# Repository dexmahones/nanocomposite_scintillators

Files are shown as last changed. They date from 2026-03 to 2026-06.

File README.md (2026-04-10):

# Scintillators for Low-Cost Pet
Documentation for a project to develop low-cost nanocomposite scintillator pixels for a PET scanner prototype. The purpose for these notes is primarily as a means of collating findings, data and progress into one piece of IP to facilitate continuity between different stages of the project. This repository consists of the following categories.
## Context
Details on the relevant theory, methodology and progress are stored in the root directory. Key notes are listed below, with links to relevant subsidiary notes embedded in them.  
- [Introduction](Introduction.md)
- [Positron Emission Tomography](PositronEmissionTomography.md)
- [Scintillator Landscape](Scintillator%20Landscape.md)
- [Scintillator Design Considerations](Scintillator%20Design%20Considerations)
- [Characterization Methods](Characterization)
## References
A growing list of [References](References.md) to useful resources is included as a kind of database of the literature consulted during the course of the project.
## Logbook
A list of the pixel fabrication techniques and trials that have already been attempted can be found in the [Fabrication Log](Logbook.md), which should be updated with any new developments.
## Manuals
A folder containing documentation and manuals (listed in [Manuals](Manuals)) for essentially any externally procured products. This includes any measurement instruments, industry standard scintillator pixels, chemical safety datasheets, quotes etc. 
## Figures
A folder to store any generated figures, both for ease of access and for embedding in these notes. 
## Data
A folder for all data taken during characterization and experimentation. 
## Code
The codebase used for this project, including data analysis, instrument control and figure generation. [Documentation](Documentation) for the code is currently in progress.
## Progress Reports
Biannual reports detailing the last six months of progress. Typically to be submitted to funders.

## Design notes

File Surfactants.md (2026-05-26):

*a.k.a ligands, capping agents*
Molecules that encapsulate nanoparticles and prevent them from aggregating. As an example, consider the CdS and CdSe nanoparticles that have been synthesized. As I understand it, two capping agents have been used, namely [oleylamine](#Oleylamine) and [oleic acid](#oleic%20acid). They are typically used to suspend the nanoparticles in [octadecene](#octadecene) and/or [toluene](#toluene) solvents. 
## Oleylamine
#ligand
- Exhibits affinity to metals through NH2 functional groups. 
- Acts as strong reducing agent as well as a stabilizer in the synthesis of nanoparticle.
![[oleylamine_structure.png]]
## Oleic Acid
#ligand
- Widely used as a surfactant for the stabilization of magnetic nanoparticles.
- Carboxyl group binds to metallic NPs in one of a number of different configurations.
![[oleic_acid_structure.png]]
## BMEP
#ligand 
- Hydrophilic monomer 
- Two polymerizable methacrylate groups 
- Centrally placed phosphate group that binds to NPs.
- It is widely used as a precursor in the synthesis of poly (BMEP), dental resins, hydrogels, and fire-retardant polymer composites.
![[bmep_structure.avif]]
Following a paper by [[References#jin2016partial|Jin et al.]] in 2016. 
- Partially exchanged OA capping YbF3 NPs with BMEP for copolymerization with PVT
![[bmep_oa_partial_exchange.png]]
### Chemicals 
- Oleic acid (OA, 90%)
- 1-octadecene (ODE, 90%), 
- ytterbium oxide (99.9%), 
- `bis[2-(methacryloyloxy)ethyl] phosphate (BMEP)`,
- vinyl toluene (VT, 99%,), 
- divinylbenzene (DVB, 80%), 
- 2-(4-tertbutylphenyl)-5-(4-biphenylyl)-1,3,4-oxadiazole (b-PBD, 99%) 
- 1,4-bis(5-phenyloxazol-2-yl) benzene (POPOP) 
- trifluoroacetic acid (TFA)
- 1,1-bis(tertbutylperoxy)-3,3,5-trimethylcyclohexane (DTTMC, 75% in aromatic free mineral spirit)
- EJ-212
### Precursor Yb(CF3COO)3 synthesis 
- Yb2O3 (10 g) powder, trifluoroacetic acid (23 ml) and DI water (23 ml) added to 250 ml flask. 
- Heated to 65°C stirred for 10 h.
- Excess trifluoroacetic acid removed by rotation evaporation to get white powder.
- Powder then dried by purging with dried argon under heating for 2 h.  
### YbF3 NP synthesis  
- Oleic acid (33.9 g) and 1-octadecene (30.3 g) added to 250 ml three-neck flask
- Degassed under vacuum for several minutes with periodic argon purging. 
- Yb(CF3COO)3 (3 g) added into the mixture under argon. 
- Solution heated to 100°C in 30 min under argon
- Vacuum pumping applied for several minutes to remove residual water and oxygen. 
- Solution was rapidly heated to 304°C and maintained at this temperature for 45 min. 
- Mixture was cooled to room temperature
- ==NPs were precipitated by the addition of acetone/hexane (4 : 1 v/v) and isolated via centrifugation at a speed of 7000 rpm for 5 min.== 
- Resulting white powder washed with ethanol three times and dried under vacuum. 
- Resulting NPs could dissolve in a low-polarity solvent well.  
### Ligand exchange of oleic acid-stabilized YbF3 NPs with BMEP  
- NP white powder (1 g) dissolved in chloroform (toluene) (10 ml)
- BMEP (59 mg) was added. 
- Kept in ice bath and for 3 h. 
- Solvent removed by rotation evaporation
- Ethanol added to precipitate the NPs, followed by centrifugation. 
- BMEP-exchanged NPs dried under vacuum at room temperature.  
### Polymer nanocomposite fabrication  
- 2 ml glass vial with 10 mm diameter modified to get a hydrophobic inner surface. 
	- Filled with hydrogen peroxide for 1 h
	- Rinsed by DI water and dried. 
	- Treated with 3 wt% solution of dimethyldichlorosilane in chloroform 30 min and dried. 
- VT monomer and DVB purified using inhibitor remover.
- For the polymer nanocomposite fabrication, 
	- Ligand exchanged NPs, 
	- a solution of VT containing 5 wt% of DVB and 
	- 1 wt% of thermal initiator DTTMC added to a Schlenk flask. 
- For the scintillator fabrication, 
	- 2 wt% of PBD and 0.02 wt% of POPOP additionally added. 
- Mixture sonicated for 15 min in ice bath and became transparent. 
- Air in Schlenk flask removed by vacuum and filled with argon. 
- Solution transferred to treated glass vial in glove box
- Capped and cured at 90°C for 24 h. 
- Transparent NP/PVT composite monolith demolded and polished.

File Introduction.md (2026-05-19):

# Context 
With the capability of examining biological processes at the metabolic level, [Positron Emission Tomography](PositronEmissionTomography.md) (PET) is a powerful medical imaging tool used for the early diagnosis of cancer as well as the assessment of a wide range of cardiovascular, neurological and metabolic disorders. Despite this versatility, South Africa only has 21 PET scanners available for a population of over 64 million - a far cry from the 2 per million people recommended by the World Health Organization. Of those, only 5 are in the state sector, which is responsible for treating 82% of potential patients, most of whom lack reliable access to relevant medical facilities. The primary reason for this undersupply of PET scanners is their prohibitively high cost of manufacturing, a major contributor of which is the monolithic crystal scintillator materials used in the PET detector modules. In the PET imaging procedure, the patient is injected with a positron-emitting radiotracer. Here, the choice of ligand species used dictates which tissues accumulate higher concentrations of the radiotracer. Positrons emitted by the radiotracer annihilate with electrons in the target tissue, producing two back-to-back gamma rays of 511 keV. A simultaneous detection of both gamma rays on opposite sides of the patient provides a line-of-response of potential locations of the initial electron-positron annihilation event. Generating a point field of annihilation events using the intersection of multiple lines-of-response results in a three-dimensional image corresponding to gamma ray activity that reveals structures in the target tissue. 
# Aim
The aim of this project is to develop a cost-effective nanocomposite scintillator material as part of a broader project to design a low-cost PET detector prototype. That means there is a secondary aim to develop an efficient yet effective fabrication process to manufacture pixels using this material to be used in the prototype scanner. Details of the specific characteristics required can be found in [Scintillator Design Considerations](Scintillator%20Design%20Considerations.md). However before discussing them in detail, it is important to formalize the problem at hand.
# Problem Statement
Fabricating a material that satisfies the unique requirements of a PET detector pixel is no trivial task, as is evident in the high cost of manufacturing for the monolithic crystals that are the current industry standard. Nevertheless, the development of nanocomposite scintillator materials has garnered substantial interest as a potential solution to this problem. By embedding trace amounts of high atomic number scintillating nanoparticles in a much cheaper host matrix, nanocomposites promise to meet the strict scintillation requirements at a substantially lower cost. However, these materials are susceptible to high rates of self-absorption caused by small nanoparticle Stoke's shift and scintillation scattering due to agglomeration during synthesis. Both of these effects are detrimental to the technical [light yield](Nomenclature.md#light-yield) and hinder detector efficiency. While fabrication methods exist to mitigate these factors, they drastically increase the complexity (and hence the cost) of manufacturing. Consequently, nanocomposite scintillators have not yet demonstrated practical relevance in real-world applications such as low-cost PET.
# Hypothesis
Developing a functional nanocomposite scintillator pixels for low-cost PET requires a holistic approach when it comes to designing a cost-effective manufacturing process. Both the strategic selection of nanoparticle, surfactant and polymer systems, and the careful consideration of efficient pixel fabrication methods are required. Controlling nanoparticle size is expected to tune the emission wavelength to match the peak quantum efficiency of the SiPM, potentially eliminating the need for secondary wavelength shifters that contribute to self-absorption while maintaining fast scintillation response times. Bifunctional capping agents with surface chemistry compatible with both nanoparticle and polymer systems enhance light yield by preventing nanoparticle agglomeration and optimizing dispersion in the matrix. Curing the resulting suspension in suitable moulds with optimal surface smoothness should simplify the pixel fabrication process by eliminating subsequent shaping and polishing procedures.
# Key Questions
- Does the replacement of wavelength shifters with tuneable nanoparticles improve technical light yield?
- What combination of bifunctional ligand and polymer maximizes nanoparticle dispersion?
- To what extent does mould surface smoothness impact pixel light yield?
- Can effective nanocomposite pixels be manufactured at a lower cost than commercially available alternatives?

So far, this remains to be seen.

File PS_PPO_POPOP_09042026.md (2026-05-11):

#logbook #fabrication
# Description
This is the second trial run for making polystyrene samples. Again, no quantum dots are added. The plan is to have another simple control of just polystyrene (PS) to compare with PS doped with PPO and POPOP, but taking into account the lessons learnt from [the first attempt](PS_PPO_POPOP_25032026.md). These were based on the following observations from the first attempt:
1. Very little polystyrene remained in the moulds after 24 hours in the oven, possibly due to evaporation.
2. Samples set in the centrifuge tubes were cloudy due to bubble formation during polymerization.
3. The styrene mixture was very fluid before being placed in the moulds. 
The current thinking is that this is primarily due to water (and/or other impurities?) remaining in the solution and then evaporating as the polymer set. The BPO, PPO and POPOP powders had quite a bit of moisture in them from the outset, and the BPO in particular is already 25% water. The following should be added to the methodology to refine the process:
4. The powders should be pre-dried
5. Any contained water should be boiled off the styrene mixture.
6. The solution should be degassed (or sonicated?) before being placed in moulds. 
7. The stoppered vials had smaller bubbles. Therefore, in this trial the silicone moulds are to be replaced with stoppered glass vials. 
Using glass vials would probably require breaking the final product out of the vials, but for now it is just a POC. In future, the use of PVA coating should be explored, as then the polystyrene could be removed by dissolving the PVA with warm water. The potential benefit of this is that the surface finish may be inherently smooth using this method ([Abe *et al*. 2026](References#abd2026pva)). 

To address these issues, the following changes are made from the first attempt:
1. **All powders are to be pre-dried** - *in the fume hood on a 40°C hot plate for 2 hrs.*
2. **Mixture is to be stirred under nitrogen** - *in fume hood with nitrogen filled balloons.*
3. **Mixing time at 80°C is to be increased to ~2 hrs** - *until solution becomes more viscous.*
4. **Replace silicone moulds with stoppered glass vials** - *to mitigate evaporation.*
5. **Samples are to be left in the oven at 80°C overnight** - *to keep a constant temperature.*
## Constituents
- 10 ml *styrene*
- 133.333 mg 75% wt. *BPO*, 25% wt. $H_2O$ 
- 100.000 mg *PPO*
- 10.000 mg *POPOP* 
>[!note] The control does not have PPO or POPOP
# Fabrication process
- Dry powders in on hot plate at 40°C for 2 hrs
>[!warning] BPO has a decomposition temperature of 70°C and is explosive when dry!
- Add to 10g (11.038 ml) of styrene
- Stir under nitrogen at 80°C for ~2 hrs - or until viscosity changes.
- Dispense 0.5ml, 0.75ml and 1ml into 1ml glass vials.
- Place in oven at 80°C overnight. 
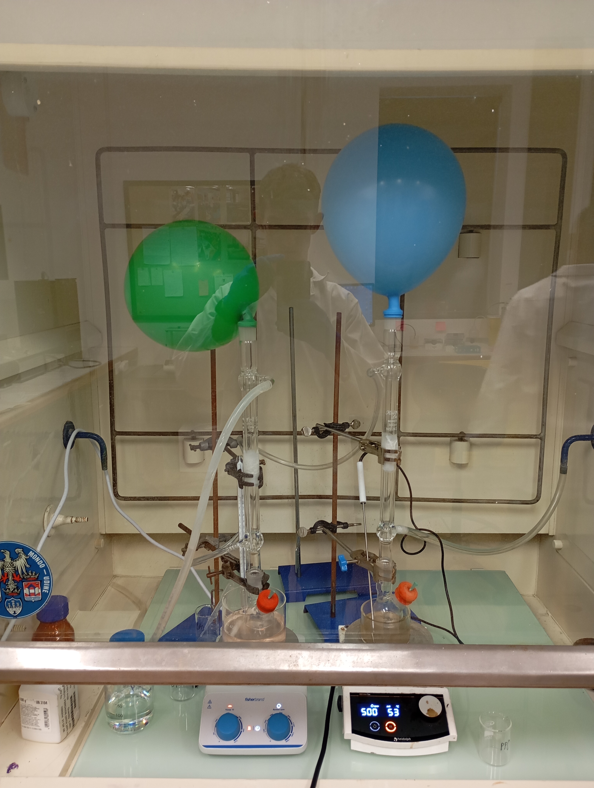
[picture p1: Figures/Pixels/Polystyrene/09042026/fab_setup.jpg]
fab_setup

# Timeline
12h50 - weighed 100 mg PPO, 133 mg BPO (x2) and 10 mg POPOP into beakers.
13h00 - dried these on hot plate at 40°C in fume hood for 2 hrs.
15h00 - added to 11 ml of styrene.
15h10 - mixture stirring at 500 rpm at 80°C in fume hood under nitrogen.
16h20 - mixture still not sufficiently viscous so continue stirring at 80°C.
16h50 - begin dispensing into vials and placing in oven at 80°C, starting with the control.
17h10 - finished dispensing scintillator into glass vials. All samples left in oven overnight.
oven

# Results
Samples were initially crystal clear at 80°C. However, switching off the oven resulted in too rapid cooling, generating stresses in the polymer that manifest as cloudiness. In regions of extreme stress, a white band (that may be a crack) can be seen. This later turned out to be a full crack through the pixel in some cases. To remedy this, half of the samples were annealed in a tube furnace set to ramp up to 100°C at a rate of 5°C per hr, hold that temperature for 2 hrs, then ramp back down at the same rate. 
>[!error] Furnace reached ~200°C in ~1 hr. Need to check PID control system.
>This also caused PS to melt and then boil, forming bubbles. 

The temperature control system for the furnace is well and truly inoperable. Another solution will have to be found.

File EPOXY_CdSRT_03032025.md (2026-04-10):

#logbook #fabrication
# Description
These samples were made using art epoxy resin and CdS quantum dots (QDs) provided by UniZulu. The `RT` indicates they were synthesized at room temperature. It is important to note that the QDs had fully dried out by the time they were used, and were not well shielded from external light sources. The idea here was to try adding a higher concentration of CdS suspended in toluene.
# Constituents
- 1.5 ml of two-part epoxy resin mixed in a ratio of A:B -> 10:6
- 8 mg of CdS RT quantum dots re-suspended in 1 ml of toluene
- Four different QD concentrations were trialed by varying the ratio of resin to toluene (CdS).
- Two sample pixels (A and B) were made for each QD concentration.

| Toluene (ml) | Resin (ml) | CdS (mg/ml) | ~ wt.% CdS | Sample ID |
| ------------ | ---------- | ----------- | ---------- | --------- |
| 0.1          | 0.9        | 0.8         | 0.1        | 3-1A/B    |
| 0.2          | 0.8        | 1.6         | 0.2        | 3-2A/B    |
| 0.3          | 0.7        | 2.4         | 0.4        | 3-3A/B    |
| 0.4          | 0.6        | 3.2         | 0.6        | 3-4A/B    |

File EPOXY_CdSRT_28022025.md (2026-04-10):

#logbook #fabrication
# Description
These samples were made using art epoxy resin and CdS quantum dots (QDs) provided by UniZulu. The `RT` indicates they were synthesized at room temperature. It is important to note that the QDs had fully dried out by the time they were used, and were not well shielded from external light sources.
# Constituents
- 1.5 ml of two-part epoxy resin mixed in a ratio of A:B -> 10:6
- 16.6 mg of CdS RT quantum dots re-suspended in 4 ml of toluene
- Four different QD concentrations were trialed by varying the ratio of resin to toluene (CdS).
- Two sample pixels (A and B) were made for each QD concentration.

| Toluene (ml) | Resin (ml) | CdS (mg/ml) | ~ wt.% CdS | Sample ID |
| ------------ | ---------- | ----------- | ---------- | --------- |
| 0.1          | 0.9        | 0.415       | 0.05       | 2-1A/B    |
| 0.2          | 0.8        | 0.83        | 0.10       | 2-2A/B    |
| 0.3          | 0.7        | 1.25        | 0.20       | 2-3A/B    |
| 0.4          | 0.6        | 1.66        | 0.30       | 2-4A/B    |

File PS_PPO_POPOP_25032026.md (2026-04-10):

#fabrication #logbook 
# Description
This was the first trial run for making polystyrene samples. No quantum dots were added. There was a simple control of just polystyrene (PS) to compare with the attempted scintillator material doped with PPO and POPOP
# Scintillator
## Constituents
- 5 ml *styrene*
- 24.160 mg 75% wt. *BPO*, 25% wt. $H_2O$ 
- 131.389 mg *PPO*
- 18.215 mg *POPOP* 
## Fabrication process
Based on the methodology from [this paper](https://onlinelibrary.wiley.com/doi/abs/10.1002/admt.202302075) by Orfano *et al.*, 2024.
>[!quote] Preparation of Polystyrene (PS) -Based Nanocomposites:
> Styrene monomer was purchased from Sigma-Aldrich (CAS no. 100-42-5) in the form of a liquid and colorless monomer. After the removal of the stabilizer, the 1,4-Bis (5-phenyl-2-oxazolyl) benzene (POPOP, Sigma Aldrich, CAS no. 1806-34-4, MW = 364.40 g mol−1) dye was dissolved with the addition of the as-prepared hafnium oxide nanoparticles. Then, the monomer polymerization followed a thermal pathway by using Azobisisobutyronitrile (AIBN), a free radical initiator, and the VAZO 64 (Chemours). The final composition was obtained as follows: 3.64 mg of POPOP and 1 mg of VAZO 64 were dissolved in 1 mL of styrene through ultrasonic stirring. Then 25 ± 1 mg of hafnium oxide nanoparticles were added to the solution and then dispersed through stirring. 
> >[!tip] We exchanged HfO2 with equivalent distribution of PPO molecules.
> 
> The as-prepared solution was placed in a temperature-controlled oil bath at 80 °C for 1 day. For the first 8 h, the mixture was mechanically stirred every hour to avoid nanoparticle sedimentation. At the end of the process, a PS-based plastic scintillator was obtained with a 10−2 m dye concentration and 2.5 + 0.1% wt hafnium oxide nanoparticles loading.

## Timeline
**11h30** -  Weighed required amount of all powder constituents into round-bottom flask. 
**12h15** - Added styrene. 
**12h30 - Submerged flask in oil bath in fume hood with water condenser "attached".
12h45 - Switched on hot plate (set to 80°C) and began stirring at 500 rpm.

>[!warning] 13h00 - Magnetic stirrer lost coherence due to contact with the flask.
>The condenser tube was too big, positioning the flask too deep in the oil bath.

>[!warning] 13h05 - Transferred solution into a smaller 2-neck round bottom flask

**13h30** - Magnetic stirrer behaved well now so started heating and stirring again 
**14h10** - Removed flask from oil bath and pipetted solution into silicone molds
14h12 - Molds placed in oven at 80°C

> [!warning] Solution was *very* fluid

**14h15** - Remainder of solution (the majority) placed back in oil bath and stirred for a further 20 min
**14h35** - Solution removed from oil bath, poured into glass centrifuge tube and placed in oven

>[!tip] Solution was more viscous

*Samples were left to cure overnight and were removed at 15h00 the following day*
# Control
## Constituents
- 5 ml *styrene*
- 24.200 mg 75% wt. *BPO*, 25% wt. $H_2O$  
## Fabrication Process
**13h35** -  Weighed required amount of BPO into 2-neck round-bottom flask. 
**13h37** - Added styrene. 
**13h40 - Submerged flask in oil bath in fume hood with water condenser.

>[!warning] Magnetic stirrer not moving
>Removed flask, started stirrer, then returned flask. Stirring kept below 300 rpm for stability.

>[!warning] No thermocouple for this hot plate
>External thermometer used, slow ramp of temperature

**14h30** - Magnetic stirrer behaved well now so started heating and stirring again. 
**14h40** - Removed flask from oil bath and pipetted solution into silicone molds
**14h45** - Remainder of solution (the majority) placed glass centrifuge tube 

> [!warning] Solution was fairly fluid

14h50 - Both placed in oven at 80°C

*Samples were left to cure overnight and were removed at 15h00 the following day*
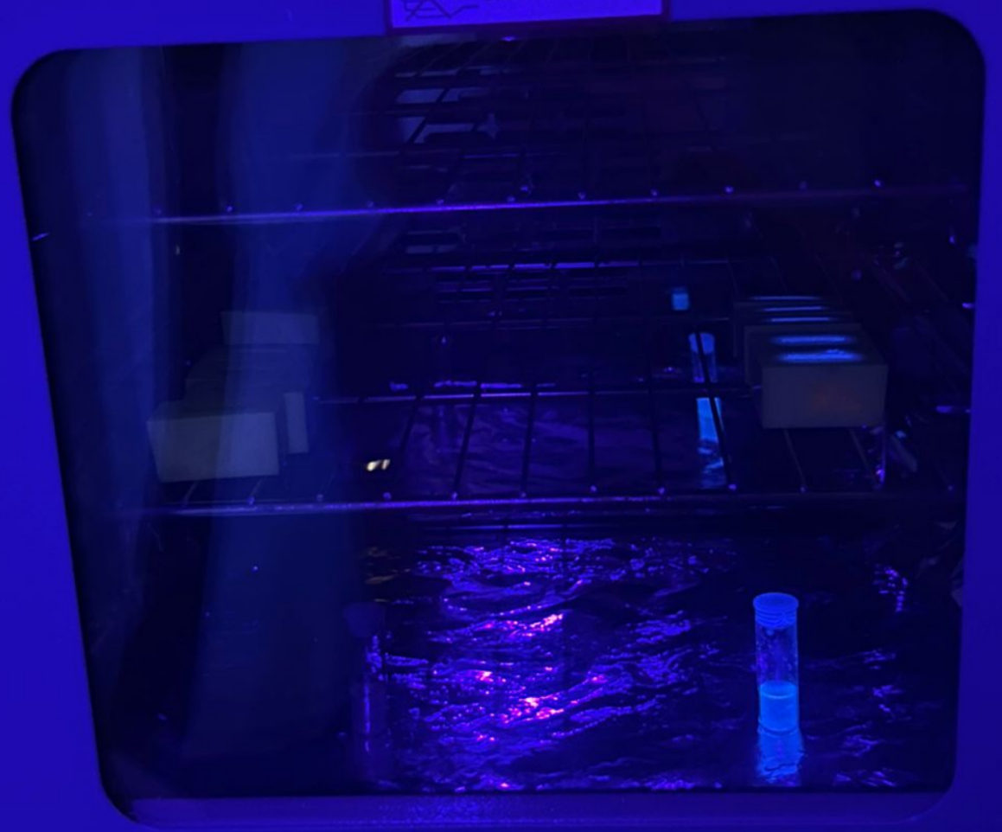
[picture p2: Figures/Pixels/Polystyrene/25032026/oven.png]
Oven

# Results
## Silicon Molds
- Very little polystyrene remained in molds. Possibly evaporated? 
- Bubbles present in scintillator samples, not present in clean samples.
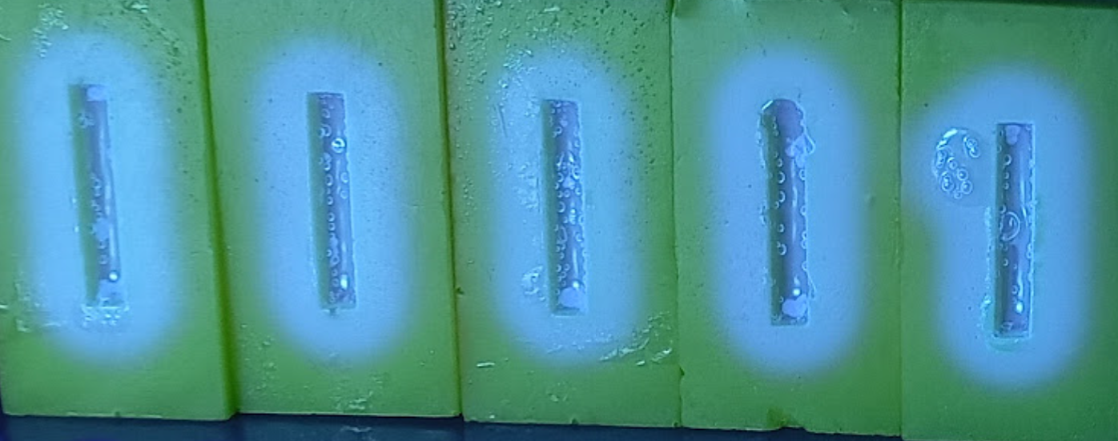
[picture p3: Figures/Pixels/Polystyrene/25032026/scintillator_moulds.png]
PS_PPO_POPOP_moulds

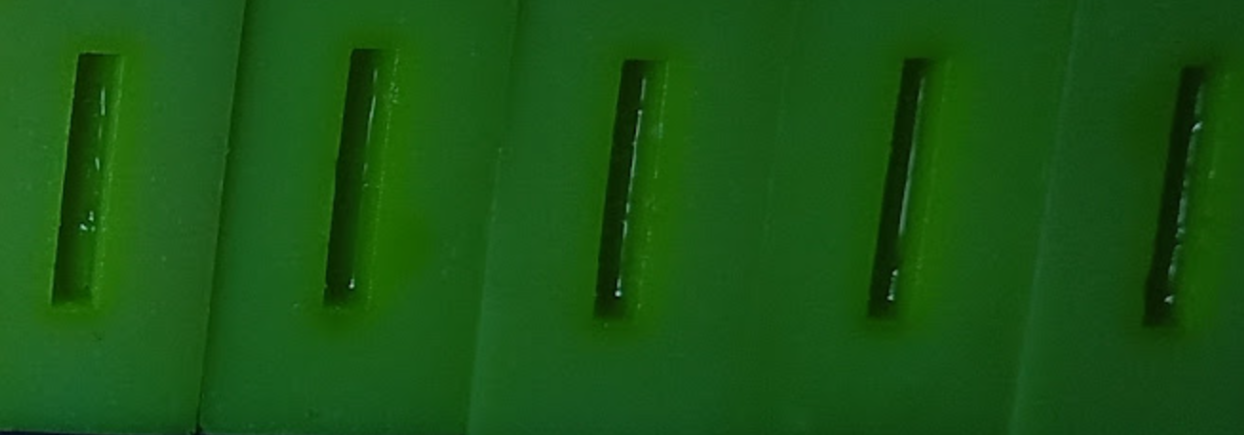
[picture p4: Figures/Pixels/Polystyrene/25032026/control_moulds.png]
PS_moulds

- Distinct overflow observed around mold boundaries.
	- Possible leaching into silicone?
	- Or simply evaporation of water?
## Glass tubes
- No visible bubbles
- Cloudy appearance - less so for the clean polystyrene
## UV illumination
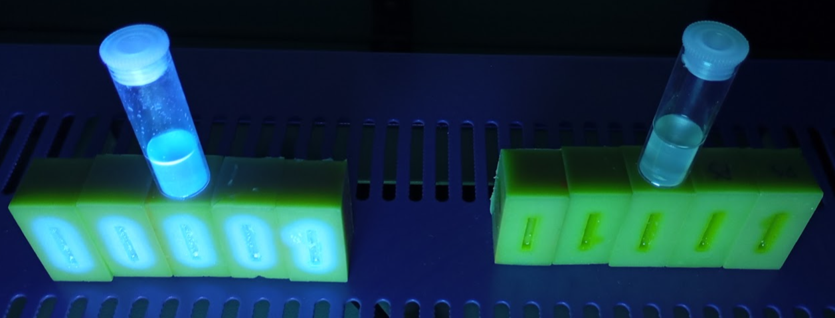
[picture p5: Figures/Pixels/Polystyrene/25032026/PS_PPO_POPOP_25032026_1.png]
UV

*UV lamp illumination of cured scintillator (left) and control (right) samples*

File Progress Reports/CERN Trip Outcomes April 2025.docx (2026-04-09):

# CERN Trip Outcomes

The primary purpose of visiting the EP-CMX group at CERN was to characterize the scintillation properties of the CdS nanocrystal embedded epoxy resin samples prepared at UCT, with the aim of identifying the optimal percentage mass concentration of CdS. This involved measuring the transmittance, emission and excitation spectra in the UV-visible range, decay time resolutions time-correlated single photon counting (TCSPC) and decay time resolution (DTR) measurements under pulsed soft X-ray excitation; and coincidence time resolution (CTR) when exposed to a source of back-to-back 511keV gamma radiation.

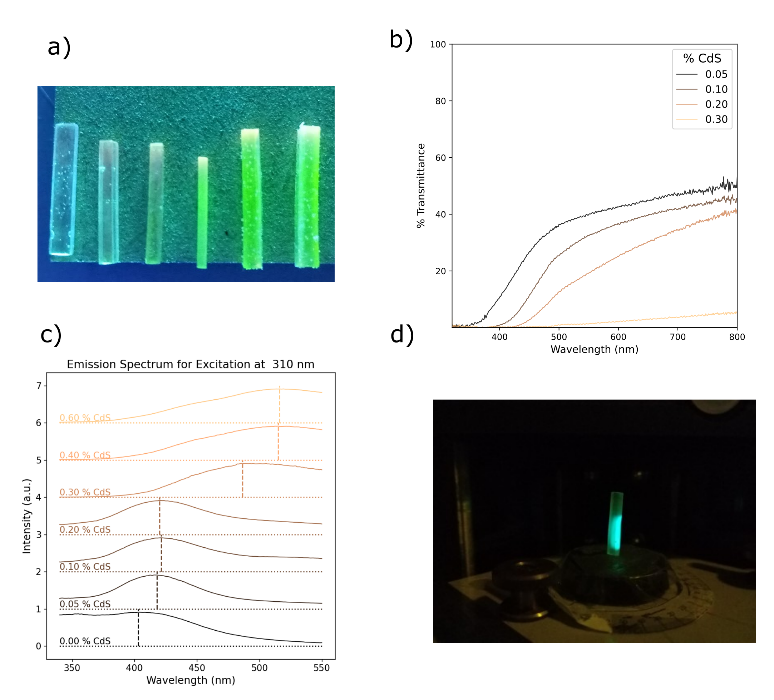
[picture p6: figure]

Figure 1: a) CdS epoxy resin samples with %CdS increasing from 0.05 - 0.6 from left to right. Transmittance (b) and emission (c) spectra for increasing CdS concentration samples. d) Sample excitation at 310 nm.

A substantial increase in opacity with increasing CdS concentration was observed in the transmittance measurements in Figure 1.b, which led to broad peaks in the emission and excitation spectra. Encouragingly, strong peaks at 420 nm were observed in the emission spectra under 310 nm excitation for CdS concentrations 0.05% - 0.20% (see Figure 1.c). This is precisely the wavelength required to optimize the scintillation signal of the silicon photomultiplier. Unfortunately, increasing the concentration further resulted in excess secondary scattering and red shift in the emission peak. This made it impossible to discern a coherent signal in the decay time measurements as they rely on high transmittance. However, TCSPC characterisation was more successful as it can be performed in reflection mode. A novel machine learning algorithm was developed to determine the decay times of multiple scintillation components using particle swarm hyperparameter optimization (PSHO), with promisingly fast effective decay time constants < 5ns for all CdS samples (see Figure 2).

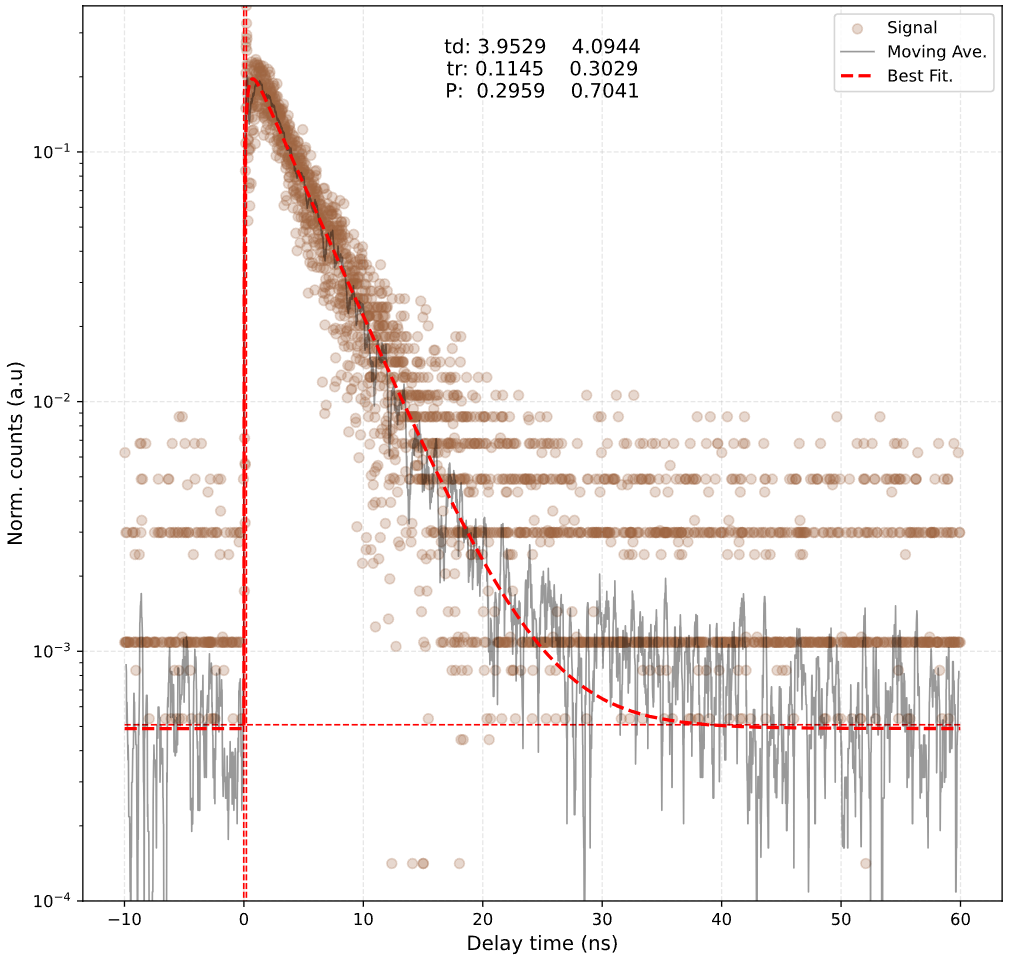
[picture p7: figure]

Figure 2: Decay time resolution < 5 ns, fit using PSHO.

Due to a lack of discernible scintillation response to the 511keV gamma rays using the CdS samples, CTR measurements were instead performed using industry standard LYSO crystal samples (see Figure 3), which will function as a vital calibration standard for the new CTR bench being set up at UCT.

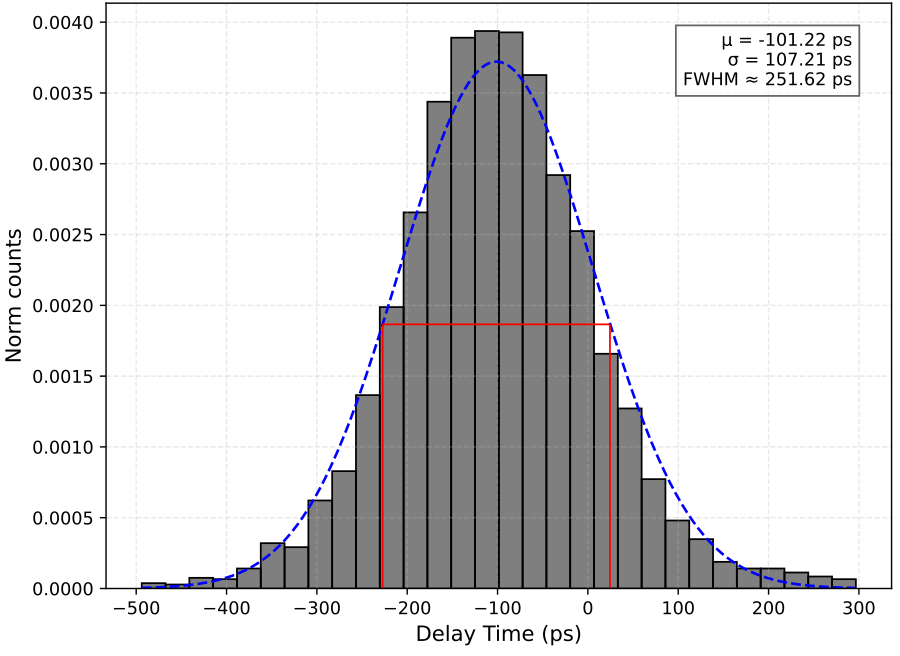
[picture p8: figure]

Figure 3: CTR of LYSO for calibration of new UCT bench.

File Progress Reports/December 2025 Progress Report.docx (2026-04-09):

End of Year Progress Report

While the initial attempt to fabricate nanocomposite scintillators by suspending CdS nanoplatelets in epoxy resin was largely unsuccessful, it provided valuable information as to what the next steps should be. The biggest limiting factor was the high self-absorption of any scintillation due to nanoparticle aggregation, so this is a key factor to mitigate in the next attempt. After extensively reviewing the literature on the subject, we have concluded that our best course of action to achieve this is to first partially exchange the nanoparticle surface ligands with a coupling agent compatible with the pixel matrix. To this end, we have decided to rather use styrene as our monomer for the matrix instead of epoxy resin, and introduce BMEP (Bis[2-(methacryloyloxy)ethyl] phosphate) as a bifunctional ligand that acts as a coupling agent to evenly disperse nanoparticles and mitigate aggregation. Additionally, we have decided to incorporate more traditional scintillator agents PPO (2,5-Diphenyloxazole) and POPOP (1,4-bis-2-(5-phenyloxazolyl)-benzene) into the matrix. The aim is to start with a proven functional scintillator, and use the nanoparticles to improve its performance, instead of attempting to circumvent traditional techniques by only relying on nanoparticles for scintillation.

Current laboratory setup for the production of polystyrene scintillator pixels at UCT.

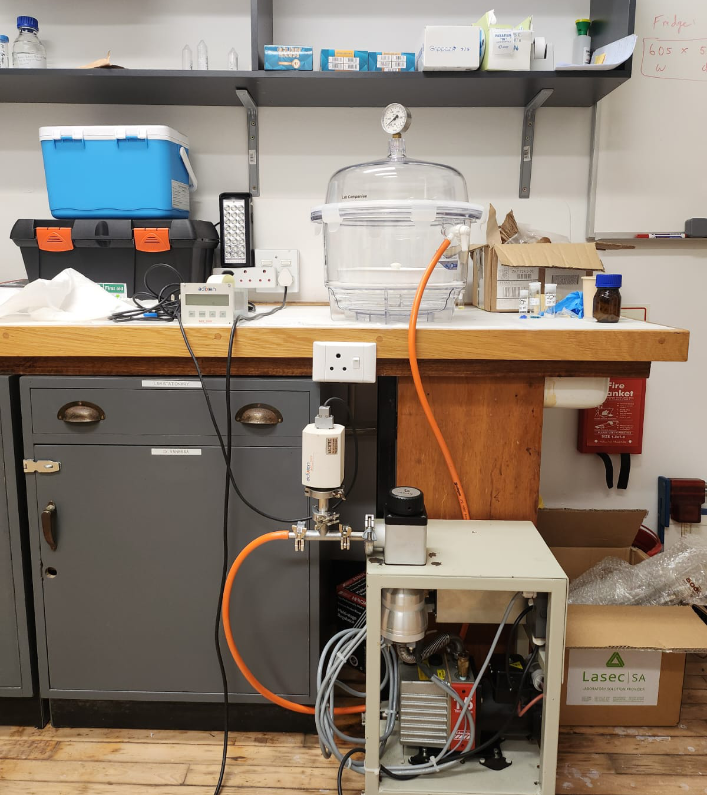
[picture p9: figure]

Thus far, we have established the laboratory setup at UCT for the production of polystyrene materials. The equipment currently in place includes a fume hood, a controlled condenser environment, a pump system, and a heating unit in Figure 2. We are presently in the proof-of-concept stage. This setup will be used to synthesize the polymer and produce scintillator pixels. This arrangement does not include a furnace, but it will be used to also prepare the prepolymer, which will then be poured into the new mold design (described below) to produce bulk pixels.

This approach differs from the current single pixel silicon molds, which allow only 1 pixel production at a time.We are currently awaiting the arrival of additional chemicals needed to proceed with the proof-of-concept work for producing scintillators at UCT.

Chemicals purchased:

- Styrene (matrix)
- PPO (primary solute)
- POPOP (wavelength shifter)
- BMEP (coupling agent)
- BPO (radical initiator) - Still pending

Figure 1: Current laboratory setup for the production of polystyrene scintillator pixel

Design of a Mold for Thermally Activated Polymerization in an Electric Furnace

Given the various methods available for polymerization—one of which involves using a furnace for bulk polymerization—I am currently designing a mold that will enable the production of multiple variations of pixels in a single batch, unlike the silicon mold we currently have. This new mold will allow a bulk cast to be fabricated and later cut into individual pixels. The design is partially complete and includes the bill of materials listed below. Fabrication will take place at UCT, and the materials still need to be purchased.

- The mold has two flat glass plates supported by an aluminum frame.
- Steel spring clamps will be used to hold the entire assembly firmly in place during the polymerization process.
- The aluminum frame includes two threaded openings:
  - One opening for pouring the prepolymer into the mold.
  - A second opening to allow air to escape during filling.
- Teflon tape gaskets are placed between the glass plates and aluminum frame to prevent leakage.

Improvements to CTR test bench

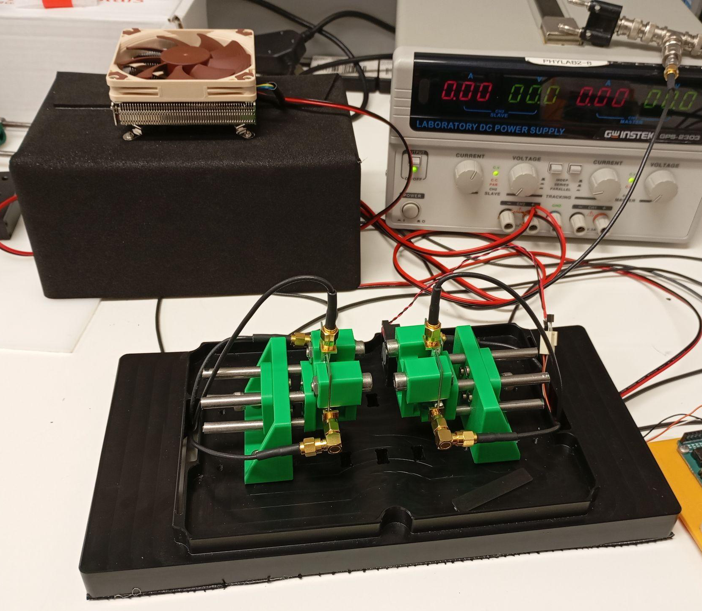
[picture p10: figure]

In preparation for the new batch of potential nanocomposite scintillators, the CTR bench has been upgraded with the following additions. The setup has been redesigned to improve alignment and is now housed inside a smaller, light-sealed darkbox. A fan-assisted peltier module in conjunction with new thermometry controls the ambient temperature inside the darkbox, mitigating SiPM response drift over time. Pixel clamps were added to improve coupling between scintillators and SiPMs, improving the signal-to-noise ratio.

Figure 2: The improved CTR Test Bench

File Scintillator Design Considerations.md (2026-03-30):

The primary challenge with PET scanner operation is the detection of those 511 keV gamma rays. Photons are typically  detected via some form of photomultiplier that converts electromagnetic waves into a coherent electronic signal. However, ionizing radiation of the kind used in PET is too energetic to effectively interact with the photomultiplier, typically requiring a few centimetres of solid lead to effectively stop 99% of 511 keV gamma rays. To solve this problem, a scintillating material capable of emitting visible photons under gamma ray excitation is coupled to the photomultiplier, effectively converting the undetectable gamma photon into a cascade of lower energy photons in the visible spectrum that can be detected. Such a material must be dense enough to reliably interact with gamma rays, yet transparent enough to allow scintillation photons to reach the photomultiplier. 

The engineering of low-cost scintillator materials is essentially a design problem, with a seemingly infinite number of solutions. It is therefore imperative to define a reasonable boundary for this problem by defining a set of requirements, constraints and criteria by which potential candidate solutions may be assessed. Defining this boundary has the added purpose of introducing key characterization techniques used to evaluate scintillator effectiveness.
# Requirements
- High [stopping power](Nomenclature#stopping-power) for the 511 *keV* gamma rays
- High [photoelectric cross-section](Nomenclature#photoelectric-cross-section) for good [energy resolution](Nomenclature#energy-resolution)
- High [light yield](Nomenclature#light-yield) - both intrinsic and technical
- Low [self-absorption](Nomenclature#Transmittance) at emission wavelength
# Constraints
- Emission wavelength must match [silicon photomultiplier (SiPM) quantum efficiency](Nomenclature#silicon-photomultiplier) (~420 nm)
- Physical dimensions - SiPMs have an active surface area of $3x3mm^2$. 
# Criteria
- [Stokes shift](Nomenclature#stokes-shift) should be as large as possible
- [Scintillation rise time](Nomenclature#rise-time) should be as short as possible
- [Scintillation decay time](Nomenclature#decay-time) should also be as short as possible
# Brief Discussion on Design Strategies
## Stopping Power
An effective scintillator must have a high stopping power for the 511 keV gamma ray products of electron-positron annihilation events. Stopping power in this context is the efficiency (or cross-section) of gamma ray absorbing interactions in the material, and is typically improved with higher atomic mass (Z) constituents. For optimal energy resolution, the cross-section of 511 keV gamma ray interaction should be high enough that a photopeak is clearly distinguishable in the energy spectrum of the scintillator. Typical organic scintillators have limited energy resolution precisely because their photoelectric interaction cross-section for gamma radiation is vanishingly small. Loading these scintillators with high-Z compounds improves the photoelectric cross-section, but still often only results in the development of a lower energy escape peak in the gamma ray energy spectrum. This is usually attributed to insufficient scintillator volume and reduced light yield. However, since this is not strictly necessary for the identification of coincident gamma interaction pairs, this requirement may be relaxed if photoelectric interactions are found to be infeasible. Energy resolution is therefore deemed to be one of the key criteria used to evaluate scintillator candidates, but is not included as a strict requirement. That being said, the material *must* exhibit a sufficiently high Compton scattering cross section to reliably scintillate under gamma irradiation. 
## Light Yield
Besides photon production from gamma ray interactions, an effective scintillator must allow the majority of scintillation photons to leave the bulk material to be detected by external photomultiplier components. Photons that are re-absorbed by the bulk material are detrimental to the performance of a PET detector module, as they do not contribute to the electronic detector signal used in coincident event detection and post-processing. Thus, the light yield of a scintillator is another key metric used to evaluate effectiveness. As with energy resolution, this metric may be considered a criterion in some contexts as it is a characteristic that can be optimized. However, it is a strict requirement that a sufficient proportion of scintillation photons leave the bulk material to trigger the desired response of the external photomultiplier detector. In order to reduce scintillation self-absorption, scintillation centers should have a *large* Stoke's shift and must not sinter or aggregate, but should rather be uniformly dispersed in the bulk matrix. Secondary wavelength shifters are often used to amplify the inherent Stoke's shift, thereby reducing self-absorption. 
## Emission Wavelength
On the subject of external scintillation detectors, the Silicon Photomultipliers (SiPM) used to convert scintillation photons into an electronic signal have a quantum efficiency that is highly dependent on the wavelength of incident light. The SiPMs used in the proposed PET detector module effectively constrains the emission wavelength of the nanocomposite scintillator to between 325 - 570 nm, with peak efficiency at 420 nm. Again, this constraint can be optimized, with emission wavelengths closer to the peak efficiency being preferred. 
## Response Time
One of the primary motivations for incorporating scintillating quantum dots into scintillating materials is the resulting enhancements in scintillation response times. Short rise- and decay-times are beneficial for sharply defined scintillation response signals, which improves the overall coincidence time resolution of a detector module. Thus, a fast scintillation response is a criterion that should be optimized, but is not a strict requirement. 
## Physical Dimensions
The final constraint is that of the physical dimensions of the detector module. The SiPMs used have an active surface area of 3x3mm$^2$. There is not necessarily a constraint on the length of pixels, it is important to keep in mind that longer pixels typically exhibit poorer light yield, while shorter pixels typically have reduced stopping power. To reliably stop 511keV gamma rays, pixels should typically be in the range of 10-20 mm in length. It may turn out to be a balancing act to find the ideal pixel length, but this may be an unnecessary detour. It is important that any fabricated pixels have the same physical dimensions for valid comparison.

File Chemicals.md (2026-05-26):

# Overview
## Quantum dots
### Core precursors
- Cadmium source
	- Cadmium acetate dihydrate (Cd(CH₃COO)₂·2H₂O) – fixed Cd source
- Sulfur source
	- Elemental sulfur (S powder, often dissolved in TOP or oleylamine) - sulfur source
- Selenium sources
	- Elemental selenium (Se powder)
	- Sodium borohydride (NaBH₄) (for in situ reduction of Se → Se²⁻)
	- Trioctylphosphine selenide (TOP-Se), if hot injection route is used
### Solvents and coordinating agents
- High-boiling solvents:
	- 1-Octadecene (ODE)
- Phosphine ligands:
	- Trioctylphosphine (TOP)
- Amine/alcohol solvents (hydro/solvothermal routes):
	- Ethanol
	- Ethylene glycol
	- Deionised water
### Capping and stabilising ligands
- Oleic acid (OA)
- 3-Mercaptopropionic acid (MPA)
### Auxiliary reagents
- Sodium hydroxide (NaOH) – for pH adjustment in aqueous synthesis
- Nitrogen (N₂) or argon (Ar) – inert atmosphere during synthesis
- Acetone, ethanol, or hexane – for washing and dispersing QDs
- Toluene  – nonpolar solvents for storing QDs
## Scintillator pixels
### Host matrix
- Styrene monomer (PS) - bulk
- 1,4-Bis(5-phenyl-2-oxazolyl)benzene (POPOP) - wavelength shifter
- 2,5-Diphenyloxazole (PPO) - primary scintillator
- Benzoyl peroxide (BPO) - polymerisation initiator
### Nanoparticle coupling agent
- `Bis[2-(methacryloyloxy)ethyl] phosphate` (BMEP)
## Consumables
- Toluene
- Hydrogen peroxide
- Ethanol
- Nitrogen
# Details 
## Oleylamine
#ligand
Oleylamine (OAm) is a long chain primary alkyamine, that acts as an electron donor at elevated temperatures. OAm exhibits affinity to metals through NH2 functional groups. FTIR spectra of OAm has been reported. Oleylamine acts as strong reducing agent as well as a stabilizer in the synthesis of nanoparticle.
![[oleylamine_structure.png]]
### Application
Used in the chemical synthesis and capping of nanoparticles such as Fe3O4, poly (2-hydroxyethyl methacrylate)-graft-poly (ε-caprolactone), titania, mesoporous silica.
### Properties

| Property         | Value                                                                                       |
| ---------------- | ------------------------------------------------------------------------------------------- |
| grade            | technical grade                                                                             |
| Quality Level    | 200                                                                                         |
| vapor pressure   | 8 mmHg ( 135 °C)                                                                            |
| assay            | 70%                                                                                         |
| composition      | primary amine, >98%                                                                         |
| refractive index | *n*20/D 1.4596 (lit.)                                                                       |
| bp               | 348-350 °C (lit.)                                                                           |
| mp               | 18-26 °C (lit.)                                                                             |
| density          | 0.813 g/mL at 25 °C (lit.)                                                                  |
| SMILES string    | `[H]\C(CCCCCCCC)=C(/[H])CCCCCCCCN`                                                          |
| InChI            | `1S/C18H37N/c1-2-3-4-5-6-7-8-9-10-11-12-13-14-15-16-17-18-19/h9-10H,2-8,11-19H2,1H3/b10-9-` |
| InChI key        | `QGLWBTPVKHMVHM-KTKRTIGZSA-N`                                                               |
## Oleic Acid
#ligand
### General description
Oleic acid (OA), a non-essential fatty acid, is classified as monounsaturated fatty acid (MUFA) richly present in olive oil. Its quantitative removal from the mixtures of triglyceride and partial glycerides has been reported. OA is widely used as a surfactant for the stabilization of magnetic nanoparticles. Monodisperse magnetite nanoparticles (7 and 19nm) coated with OA have been prepared.
![[oleic_acid_structure.png]]
### Application
Oleic acid has been used:  
- to study the effects of fatty acids on gastric cancer (GC)
- to induce lipid droplet formation in cell culture
- as an additive in the magnetorheological fluid preparation.
Oleic acid may be used in the preparation of 10-hydroxy octadecanoic acid and methyl ester of the 10-hydroxy octadecanoic acid.
### Properties
|Property|Value|
|---|---|
|biological source|plant (Sunflower)|
|Quality Level|/life-science/quality-and-regulatory-management/m-clarity-program|
|vapor pressure|1 mmHg ( 176 °C)|
|assay|≥99% (GC)|
|form|viscous liquid|
|color|colorless to very faintly yellow|
|refractive index|_n_20/D 1.459 (lit.)|
|bp|194-195 °C/1.2 mmHg (lit.)|
|mp|13-14 °C (lit.)|
|solubility|H₂O: insoluble (practically), alcohol: soluble, benzene: soluble, chloroform: soluble, oil: soluble (fixed and volatile)|
|density|0.89 g/mL at 25 °C (lit.)|
|application(s)|life science and biopharma  <br>lipidomics|
|functional group|oleic acid|
|lipid type|unsaturated FAs|
|shipped in|ambient|
|storage temp.|−20°C|
## BMEP
#ligand 
`Bis[2-(methacryloyloxy)ethyl] phosphate` (BMEP) is a hydrophilic monomer with two polymerizable methacrylate groups and a centrally placed phosphate group. In presence of an acid, it can undergo spontaneous polymerization with a high degree of conversion. It is widely used as a precursor in the synthesis of poly (BMEP), dental resins, hydrogels, and fire-retardant polymer composites.
![[bmep_structure.avif]]
### Application

`Bis[2-(methacryloyloxy)ethyl]` phosphate (BMEP) can be used:

- As a bifunctional crosslinker to synthesize superabsorbent polymers (SAPs) via free radical polymerization. These SAPs can be used for agricultural applications.
- To prepare self-etching primer formulations for enamel and dentine. Primers with BMEP exhibit good wetting, etching, and penetration in both dentine and enamel.
- As a precursor to synthesize fire retardant nanocomposites via suspension polymerization.
### Features and Benefits
- Presence of dimethacrylate groups enables cross-linking and improves copolymerization.
- Hydrophilicity and short carbon chains can enhance wetting.
### Properties
| Property         | Value                                                                                            |
| ---------------- | ------------------------------------------------------------------------------------------------ |
| refractive index | _n_20/D 1.47 (lit.)                                                                              |
| Quality Level    | 200                                                                                              |
| bp               | 221 °C (lit.)                                                                                    |
| density          | 1.28 g/mL at 25 °C (lit.)                                                                        |
| storage temp.    | 2-8°C                                                                                            |
| SMILES string    | `CC(=C)C(=O)OCCOP(O)(=O)OCCOC(=O)C(C)=C`                                                         |
| InChI            | `1S/C12H19O8P/c1-9(2)11(13)17-5-7-19-21(15,16)20-8-6-18-12(14)10(3)4/h1,3,5-8H2,2,4H3,(H,15,16)` |
| InChI key        | `NXBXJOWBDCQIHF-UHFFFAOYSA-N`                                                                    |
## Octadecene
#solvent
![[octadecene_structure.png]]
### Application
- **Chromatographic applications:** 1-Octadecene is utilized in the design of smart temperature-sensitive terpolymeric hydrogels for diverse applications in liquid chromatography, enhancing phase separation and analytical performance ([Zhao et al., 2024](https://doi.org/10.1016/j.chroma.2024.464867)).
- **Enhancement of optical materials:** Used in the stabilization of perovskite nanocrystals, 1-Octadecene contributes to significant improvements in the optical performance of these materials, relevant in display technology and photovoltaics ([Bommireddy et al., 2024](https://doi.org/10.1016/j.heliyon.2024.e24497)).
- **Quantum dot synthesis:** The compound facilitates the synthesis of CdSe quantum dots for polymer optical fiber technology, showing its critical role in the development of advanced optical materials ([Kiczor and Mergo, 2023](https://doi.org/10.3390/ma17010227)).
### Analysis Note
Assay (GC, area%): ≥ 91.0 % (a/a)  
Density (d 20 °C/ 4 °C): 0.788 - 0.790  
Identity (IR): passes test  
Due to its specific melting range the product may be solid, liquid, a solidified melt or a supercooled melt.
### Properties
| Property            | Value                                                                      |
| ------------------- | -------------------------------------------------------------------------- |
| vapor pressure      | 1.3 hPa ( 20 °C)                                                           |
| Quality Level       | /life-science/quality-and-regulatory-management/m-clarity-program          |
| assay               | ≥91.0% (GC)                                                                |
| form                | liquid                                                                     |
| potency             | >10000 mg/kg LD₅₀, oral (Rat), >10000 mg/kg LD₅₀, skin (Rabbit)            |
| kinematic viscosity | 3.6 cSt(40 °C)                                                             |
| bp                  | 315 °C/1013 hPa                                                            |
| mp                  | 17-18 °C                                                                   |
| transition temp     | flash point 154 °C                                                         |
| density             | 0.79 g/cm³ at 20 °C                                                        |
| storage temp.       | 2-30°C                                                                     |
| SMILES string       | `C(CCCCCCCC)CCCCCCCC=C`                                                    |
| InChI               | `1S/C18H36/c1-3-5-7-9-11-13-15-17-18-16-14-12-10-8-6-4-2/h3H,1,4-18H2,2H3` |
| InChI key           | `CCCMONHAUSKTEQ-UHFFFAOYSA-N`                                              |
## Toluene
#solvent
![[toluene_structure.png]]
### General description
Our premium ACS solvents are ideal for routine chemical synthesis, drying, purification, and critical labware cleaning. They meet or exceed the rigorous standards of the American Chemical Society (ACS), ensuring high-quality results for your research needs.  
  
**Premium ACS Solvents:** Our solvents meet or exceed the stringent standards set by the American Chemical Society, ensuring high quality and reliability for your laboratory applications.  
  
**Replicable and Publishable Results:** Designed for consistency, our solvents deliver results that can be reliably reproduced, making them ideal for research that requires publication.  
  
**Versatile Applications:** Suitable for routine chemical synthesis, drying, purification, and critical labware cleaning, our solvents cater to a wide range of research needs in the laboratory.  

Toluene, a flammable liquid with a pungent odor, is widely employed as organic solvent. It is widely used as a precursor for synthesizing benzene and as a solvent in the paint industry. It has been reported to be a biotoxic solvent (toxic to many microorganisms at 0.1%v/v concentrations). Its anaerobic biodegradation to CO2, by the denitrifying bacterium _Thauera arornatica_ has been reported. It forms a syndiotactic polystyrene-toluene molecular compound. Crystal structure of this molecular compound has been investigated by X-ray diffraction studies.
### Application

Toluene has been employed as an solvent for the asymmetric synthesis of propargylic alcohols via addition reaction of terminal alkynes with various aldehydes in the presence of an optically active reagent, _N_-methylephedrine. It may be used in the preparation of amine-capped gold nanocrystals. Toluene undergoes alkylation in the presence of modified ZSM (Zeolite Socony Mobil)-5-class zeolite catalysts to form _p_-xylene with high selectivity. When doped on graphene, it acts as an electron donor leading to alteration in graphene electrical properties.
### Properties
| Property           | Value                                                               |
| ------------------ | ------------------------------------------------------------------- |
| grade              | ACS reagent                                                         |
| Quality Level      | /life-science/quality-and-regulatory-management/m-clarity-program   |
| agency             | suitable for EPA 1613                                               |
| vapor density      | 3.2 (vs air)                                                        |
| vapor pressure     | 22 mmHg ( 20 °C), 26 mmHg ( 25 °C)                                  |
| assay              | ≥99.5%                                                              |
| form               | liquid                                                              |
| autoignition temp. | 997 °F                                                              |
| expl. lim.         | 7 %                                                                 |
| dilution           | (for analytical testing)                                            |
| impurities         | H₂SO₄, passes test (darkened), ≤0.003% _S_ compounds, ≤0.030% water |
| evapn. residue     | ≤0.0010%                                                            |
| color              | APHA: ≤10                                                           |
| refractive index   | _n_/D 1.496 (lit.)                                                  |
| bp                 | 110-111 °C (lit.)                                                   |
| mp                 | -93 °C (lit.)                                                       |
## MPA
#ligand 
### Description
3-Mercaptopropionic acid (3-MPA) is used as a self-assembled monolayer (SAM) with a thiol and carboxylic groups. It has short carbon chains and is mainly used as a capping agent on a variety of nanoparticles.
![[mpa_structure.png]]
### Application
3-MPA is used to produce hydrophilic SAMs, which are terminated with carboxylic acids and can be further functionalized to introduce more complex end groups such as enzymes for biosensor applications. SAMs of 3-MPA are capped on ZnSe quantum dots for the electrochemical detection of dopamine. 3-MPA is used as a capping agent on CdTe quantum dot nanocrystals (QD NCs) for use as labeling materials in biomedical applications. It can also be used to modify the surface of iron oxide nanoparticles (Fe2O3) in the extraction and preconcentration of Al3+ and Cr3+ ions from different biological samples.
### Properties
| Property | Value |
| --- | --- |
| vapor pressure | 0.04 mmHg ( 20 Â°C) |
| Quality Segment | 200 |
| assay | â‰¥99% |
| form | liquid |
| autoignition temp. | 662 Â°F |
| refractive index | n20/D 1.492 (lit.) |
| bp | 110-111 Â°C/15 mmHg (lit.) |
| mp | 15-18 Â°C (lit.) |
| density | 1.218 g/mL at 25 Â°C (lit.) |
| SMILES string | OC(=O)CCS |
| InChI | 1S/C3H6O2S/c4-3(5)1-2-6/h6H,1-2H2,(H,4,5) |
| InChI key | DKIDEFUBRARXTE-UHFFFAOYSA-N

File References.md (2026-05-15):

#### sahi2017high
High-loaded and transparent LaxCe1-xF3 - polystyrene nanocomposite scintillators for radiation detection 
*Sahi et al.* (2017) [DOI 10.1139/cjc-2017-0211](https://research.ebsco.com/linkprocessor/plink?id=eee84485-4ec6-3a54-9b57-9b5c49ae7154)
#### turtos2019on
On the use of CdSe scintillating nanoplatelets as time taggers for high-energy gamma detection 
*Turtos et al.* (2019) [DOI 10.1038/s41699-019-0120-8](https://www.nature.com/articles/s41699-019-0120-8)
#### tam2021integrated
Integrated and Portable Probe Based on Functional Plastic Scintillator for Detection of Radioactive Cesium
*Tam et al.* (2021) [DOI 10.3390/app11115210](https://www.mdpi.com/2076-3417/11/11/5210)
#### li2023bulk
Bulk Polystyrene-BaF2 Composite Scintillators for Highly Efficient Radiation Detection 
*Li et al.* (2023) [DOI 10.3390/cryst13091334](https://www.mdpi.com/2073-4352/13/9/1334)
#### li2023ultrafast
Ultrafast and Radiation-Hard Lead Halide Perovskite Nanocomposite Scintillators 
*Li et al.* (2023) [DOI 10.3390/cryst13091334](https://www.mdpi.com/2073-4352/13/9/1334)
#### morfano2024fast
Fast emitting nanocomposites for high-resolution ToF-PET imaging based on multicomponent scintillators  
*Morfano et al.* (2024) [DOI 10.1002/admt.202302075](https://onlinelibrary.wiley.com/doi/abs/10.1002/admt.202302075)
#### shamraienko2025expanding
Expanding the Family of Heterostructured CdSe/CdS Core/Crown Nanoplatelets: Six- and Seven-Monolayers-Thick Species
*Shamraienko et al.* (2025) [DOI 10.1021/acs.chemmater.5c00650](https://pubs.acs.org/doi/10.1021/acs.chemmater.5c00650)
#### winardi2024nanocomposite
Winardi, Isabelle, Ziqing Han, Hao Yu, Prabhav Surabhi, and Qibing Pei. “Nanocomposite Scintillators Loaded With Hafnium Oxide and Phosphorescent Host and Guest for Gamma Spectroscopy.” _Chemistry of Materials_ 36, no. 10 (2024): 5257–63. [https://doi.org/10.1021/acs.chemmater.4c00805](https://doi.org/10.1021/acs.chemmater.4c00805).
#### liu2017transparent
Liu, Chao, Zhou Li, Tibor Jacob Hajagos, David Kishpaugh, Dustin Yuan Chen, and Qibing Pei. “Transparent Ultra-High-Loading Quantum Dot/Polymer Nanocomposite Monolith for Gamma Scintillation.” _ACS Nano_ 11, no. 6 (2017): 6422–30. [https://doi.org/10.1021/acsnano.7b02923](https://doi.org/10.1021/acsnano.7b02923)
# jin2016partial
Jin et al., “Partial Ligand Exchange as a Critical Approach to the Synthesis of Transparent Ytterbium Fluoride–Polymer Nanocomposite Monoliths for Gamma Ray Scintillation.” [https://doi.org/10.1039%2Fc6tc00447d](https://doi.org/10.1039%2Fc6tc00447d)
# pagano2022a
F. Pagano _et al._, “A new method to characterize low stopping power and ultra-fast scintillators using pulsed X-rays,” _Front. Phys._, vol. 10, Oct. 2022, doi: [10.3389/fphy.2022.1021787](https://doi.org/10.3389/fphy.2022.1021787).
# abd2026pva
Abe, Yuma, Daiki Fukai, Taro Toyoda, Naoto Fukumoto, and Kyohei Terao. “PVA-Coated 3D-Printed Molds for Rapid Prototyping of PDMS Microdevices for Stem Cell Culture.” _Biomedical Microdevices_ 28, no. 1 (2026): 10. [https://doi.org/10.1007/s10544-026-00790-5](https://doi.org/10.1007/s10544-026-00790-5).
# li2023bulk
Li, Xiang, Mingxue Deng, Yun Shi, et al. “Bulk Polystyrene-BaF2 Composite Scintillators for Highly Efficient Radiation Detection.” _Crystals_ 13, no. 9 (2023). [https://doi.org/10.3390/cryst13091334](https://doi.org/10.3390/cryst13091334).

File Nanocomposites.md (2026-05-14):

Nanocomposite materials are typically made up of nanoparticles and various optical constituents dispersed in a solid [matrix](Nomenclature#Matrix) of some kind. The matrix is ideally ultra-transparent to minimize [self-absorption](Nomenclature#Self-absorption) and maximize the amount of light that reaches the [SiPM](Nomenclature#SiPM). The optical elements are molecules embedded in the matrix with the express purpose of transferring the undetectable energy of the 511 keV gamma ray into a cascade of photons that fall within the SiPMs sensitivity range. This happens via a network of energy transfer mechanisms that can be radiative ([FRET](Nomenclature#FRET)) or non-radiative ([DET](Nomenclature#DET)). To explain this process, it is useful to consider the chain of events triggered by a gamma ray interaction.
## Scintillation Process
A gamma ray deposits its large amount of energy via interactions with the various components of a material, generating a host of singlet and triplet excitons in the material. The decay of an excited singlet state back to the ground state emits visible light, but the excited triplet state decays via a nonradiative transition that requires a non-radiative energy transfer mechanism to a secondary scintillation center to ultimately produce photons of the desired wavelength. Even radiative decay mechanisms generally rely on secondary scintillation centers to shift the emitted photon wavelength toward the quantum efficiency peak of the SiPM. The constituents of the composite scintillator are therefore typically divided into two categories: the [host](#Host) and the [dopant](#Dopant). Here it is understood that the host is responsible for initially stopping the gamma ray (i.e. capturing its energy) and then transferring that energy to the dopant, which then fluoresces. 

A good description of the FRET processes involved is given by [Liu *et al.*](References#liu2017transparent) while both FRET and DET processes are described by [Winardi *et al.*](References#winardi2024nanocomposite). The general (idealized) process is as follows. 
1. The incident gamma photon imparts energy to an embedded nanoparticle, emitting an electron via the photoelectric effect.
2. The resulting photoelectron propagates through the material exciting host constituents (matrix molecules, nanoparticles, primary scintillation centers). 
3. Excited constituents decay, transferring energy to dopant molecules, thereby exciting them.
4. Excited dopants decay radiatively via photon emission.
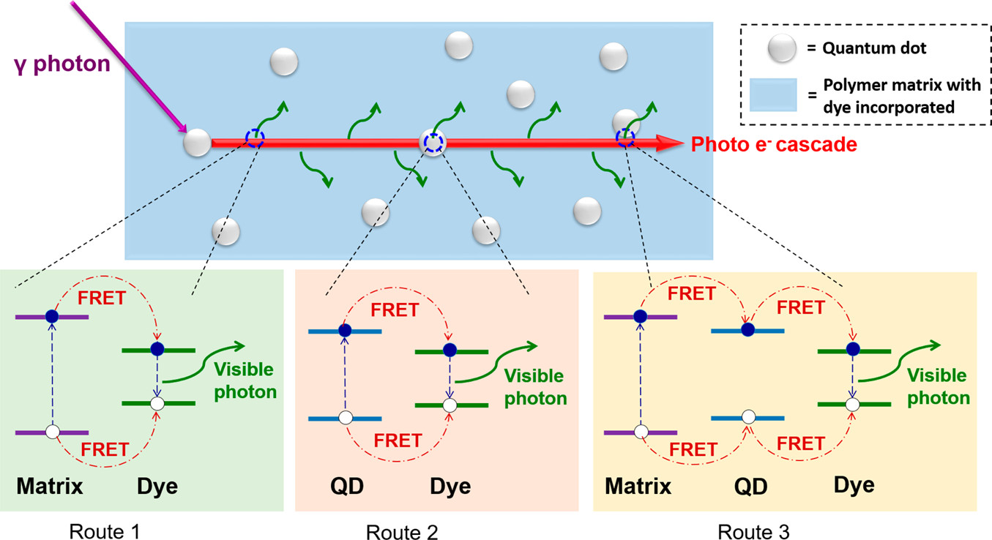
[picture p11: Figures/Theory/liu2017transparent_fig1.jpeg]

*Figure: Schematic of energy transfer processes take from [Liu et al.](References#liu2017transparent)*
# Constituents
## Host
### Matrix
- Structural integrity
- Light guide
- Maintain particle dispersion
- Gamma interactions
### Nanoparticles
*a.k.a. [Quantum dots](Nanoparticles)*
- Gamma interaction
- Photoelectron production
- Primary scintillation
### Primary Scintillation Centers
- Provide additional routes for energy transfer to dopant molecules. 
## Dopant
*a.k.a. Dye, Wavelength shifter, Secondary Fluor*
- Fluorescence at optimal wavelength
- Increase overall [Stokes shift](Nomenclature#stokes-shift) 
# Fabrication
One of the primary challenges with fabricating nanocomposites is overcoming nanoparticle aggregation. Essentially, this describes the joining of two or more nanoparticles into a larger cluster that has a greater propensity for reabsorbing or scattering photon emissions. Aggregation is thus detrimental to transmittance and ultimately reduces technical light yield. The key strategy for preventing aggregation is to encapsulate each nanoparticle in specifically coated [surfactants](Surfactants.md) (a.k.a ligands) to act as a buffer between the metallic nanoparticles. For ideal dispersion in an emulsion, the surfactants should be bifunctional, with one functional group binding strongly to the nanoparticle, and the other being soluble in the solvent of choice. In the case of embedding nanoparticles in a polymer matrix, the ligand should have a functional group that allows it to copolymerize with the polymer chains. If the nanoparticles cannot be synthesized in a suspension of the plastic monomer, then whatever surfactants are used during synthesis will have to be (at least partially) exchanged before polymerization. This means the metallic-binding functional groups should not bind too strongly to the nanoparticles, or at least that they should be removable, or exchangeable.

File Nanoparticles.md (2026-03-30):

# Nanoplatelets (NPL)
## Core-shell
>[!quote] ...continuous growth...over the entire surface of...NPLs at high temperatures, can lead to an increase in photoluminescence quantum yield (PLQY) and optical stability by passivating surface defects [[References#Expanding the Family of Heterostructured CdSe/CdS Core/Crown Nanoplatelets Six- and Seven-Monolayers-Thick Species| ref]].
## Core-crown
>[!quote]  Crown growth...focuses on the passivation of defects at the edges of the NPLs, whereby the thickness of the core/crown heterostructure remains the same as for the core NPLs and only leads to an increase in the lateral  dimensions [[References#Expanding the Family of Heterostructured CdSe/CdS Core/Crown Nanoplatelets Six- and Seven-Monolayers-Thick Species| ref]].

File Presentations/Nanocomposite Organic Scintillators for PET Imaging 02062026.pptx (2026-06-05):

## Nanocomposite Organic Scintillators for PET Imaging

Declan Mahony, James Keaveney, Mark Blumenthal

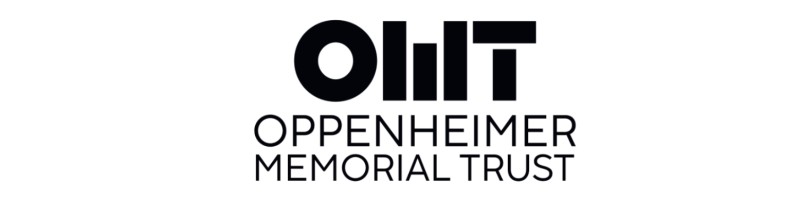
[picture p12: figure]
Tracey Webster - Chief Executive Officer - Oppenheimer Memorial Trust | LinkedIn

## Outline

Context
How scintillators work
What makes a good scintillator
Scintillator landscape
Motivation for nanocomposites
Progress and Challenges

## The Big Question

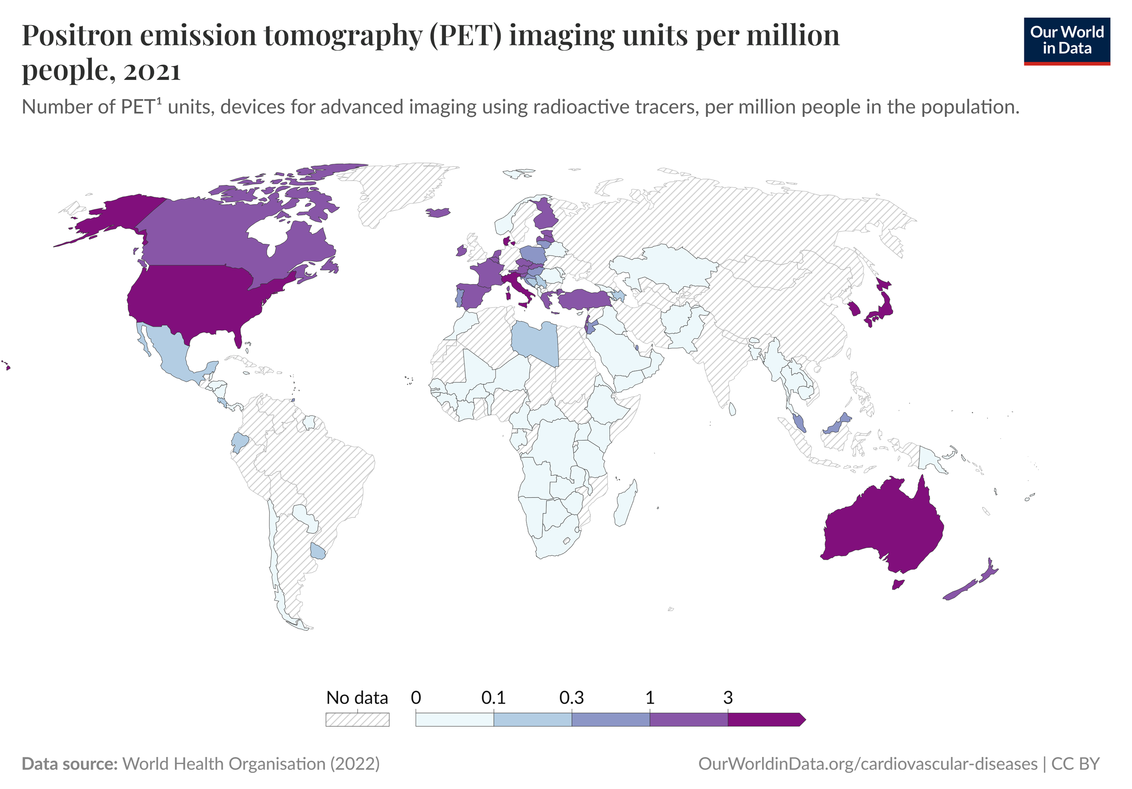
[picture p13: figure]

How do we make PET cheaper and more accessible?
Make cheaper scintillators?

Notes: Why are they expensive?
How can we make them cheaper?

## What scintillators do

Detection

Transmission

Processing

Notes: In this case, we are “seeing” gamma rays

## How scintillators work

e

e

e

Absorption

h

Energy Transfer

h

Luminescence

h

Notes: Talk about the excitation and decay of electrons (excitons) here.

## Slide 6

How scintillators work

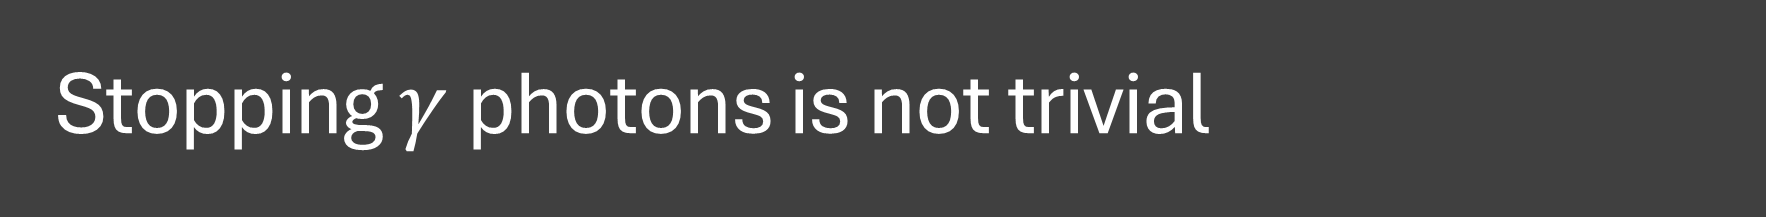
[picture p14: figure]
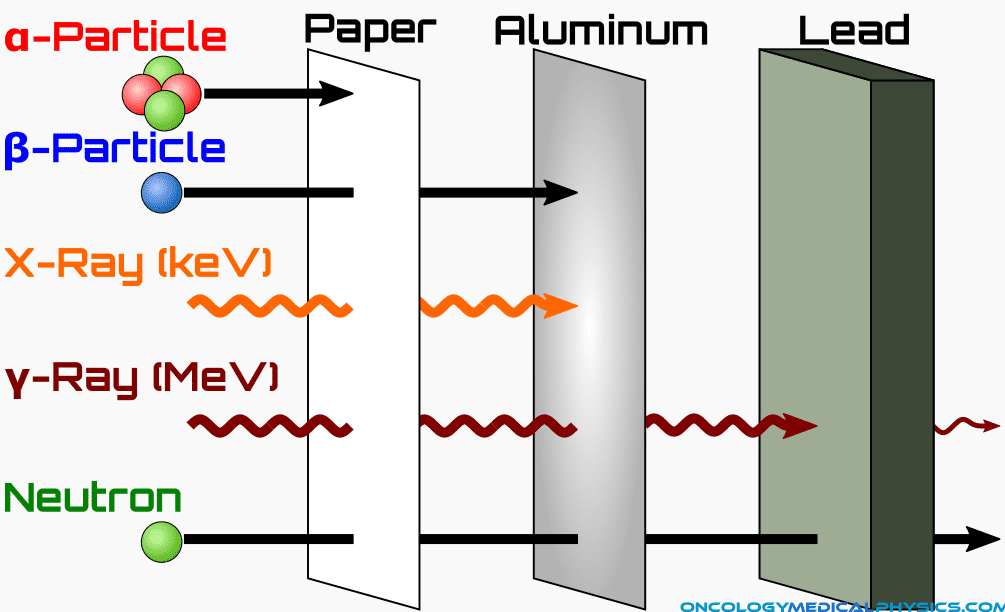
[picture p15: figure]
Differential attenuation method of determining radioactive decay products.

## Absorption

How scintillators work

Photoelectric Effect
σ_p ≈(Z^3)/(E^3)
Compton Scattering
σ_c ≈ρ_e
Exciton creation

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
Conduction Band

Valence Band

## Absorption

How scintillators work

Secondary scatters
γ energy depletion
Exciton cascade

Conduction Band

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
Valence Band

## Energy Transfer

How scintillators work

Non-radiative excitation of active centers
Exciton recombination
Lattice vibrations (heat)
Förster/Dexter energy transfer

Host Matrix

Defect

Active center

Detector

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
Phonon

h

h

## Luminescence

How scintillators work

Relaxation of active centers.
Photon emission.
Transmitted out.

Host Matrix

Defect

Active center

Detector

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
Phonon

h

h

Photon

## Losses

How scintillators work

Phonon emission
Self-absorption
Scattering

Host Matrix

Self-absorption

Detector

e

e

e

e

e

e

Phonon

h

h

h

h

h

h

Scattering

## What makes a good scintillator

Light Yield
Fast Scintillation
Energy Resolution

## Recap

What makes a good scintillator

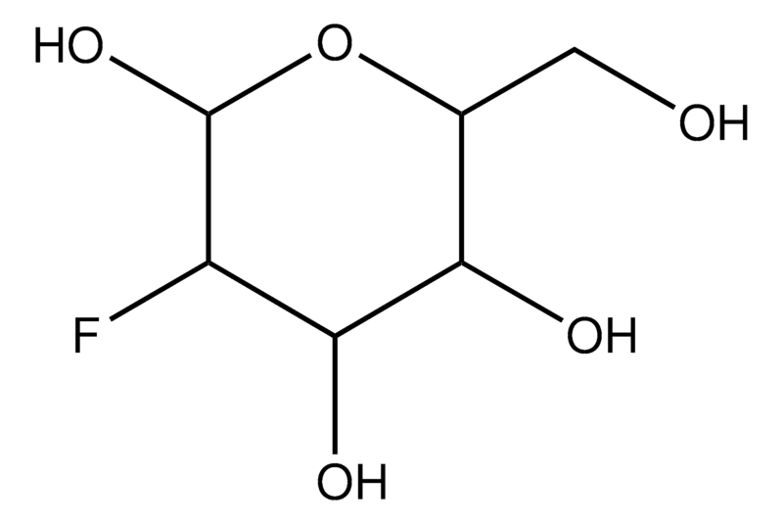
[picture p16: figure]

See the γ→ see the tumour

Fluorodeoxyglucose

511 keV

e^(+)

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
818O

511 keV

e^(−)

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
918F

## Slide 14

What makes a good scintillator

Noisy complications

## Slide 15

What makes a good scintillator

Noise Elimination

Add another camera
Coincidence timing
Fast scintillation

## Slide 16

What makes a good scintillator

Noise Elimination

Add another camera
Coincidence timing
Fast scintillation
Filter by Energy
Photopeak identification
Energy resolution

## Light Yield

What makes a good scintillator

High stopping power
Density
Atomic number
High transparency
Low self-absorption
Minimal scattering

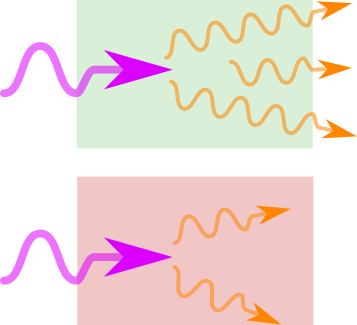
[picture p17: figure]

## Fast scintillation

What makes a good scintillator

Fast exciton decay
Short recombination length
Concentrated active centers
Efficient FRET/DET
Minimal energy transfer paths
Strong quantum resonance

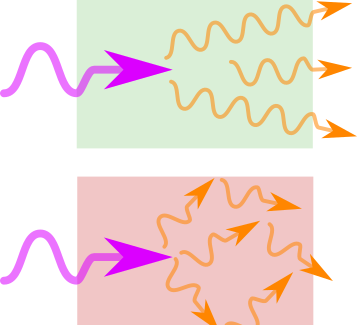
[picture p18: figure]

## Energy Resolution

What makes a good scintillator

High stopping power
Reduce radiation escape
Photoelectric interaction σ
High Z
σ_(pe) ≈(Z^3)/(E^3)

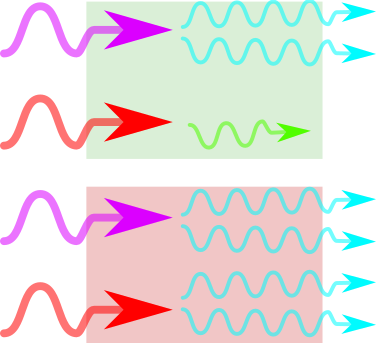
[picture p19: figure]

## Scintillator Landscape

Crystals
Organics
Ceramics

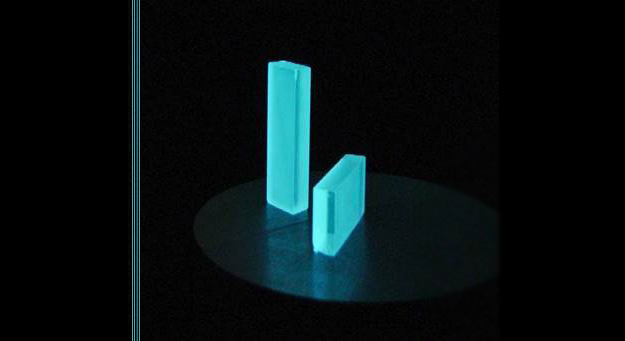
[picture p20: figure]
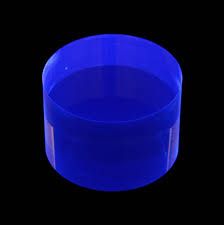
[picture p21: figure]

## Crystals

Scintillator Landscape

Stopping power – 1 cm attenuation (high Z)
Energy resolution – photoelectric events
Fast scintillation – 40 ns decay time
Transparent – 32 000 photons/MeV light yield
Expensive

## Organics

Scintillator Landscape

Stopping power – 10 cm attenuation (low Z)
Energy resolution – NO photoelectric events
Fast scintillation – 2 ns decay time
Transparent – 10 000 photons/MeV light yield
Expensive

## Ceramics

Scintillator Landscape

Stopping power – 10 cm attenuation (high Z)
Energy resolution –photoelectric events
Slow scintillation – 1 μ s decay time
Opaque – 20 000 photons/MeV light yield
Inexpensive

## Motivation for Nanocomposites

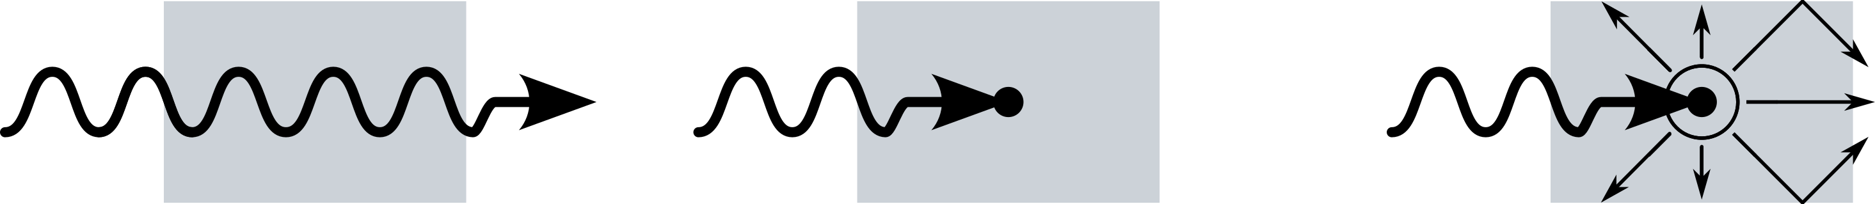
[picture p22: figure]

Cheap polymer host matrix

Small, dense activation centres

Fast scintillation

## Nanoparticle Activation Centers

Motivation for Nanocomposites

Spatially confined excitons
Fast scintillation
High Z
Large γ cross-section
Photoelectric interactions
Tuneable excitation/emission

Host Matrix

e

e

γ

h

h

## Nanocomposite plastic

Motivation for Nanocomposites

Stopping power – High Z
Energy resolution –photoelectric events
Fast scintillation – 1 ns decay time
Transparent? – High self-absorption and scattering
Inexpensive?

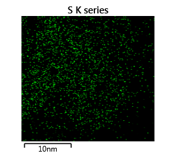
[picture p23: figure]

## Trial #1 – Epoxy Resin + CdS Nanoplatelets

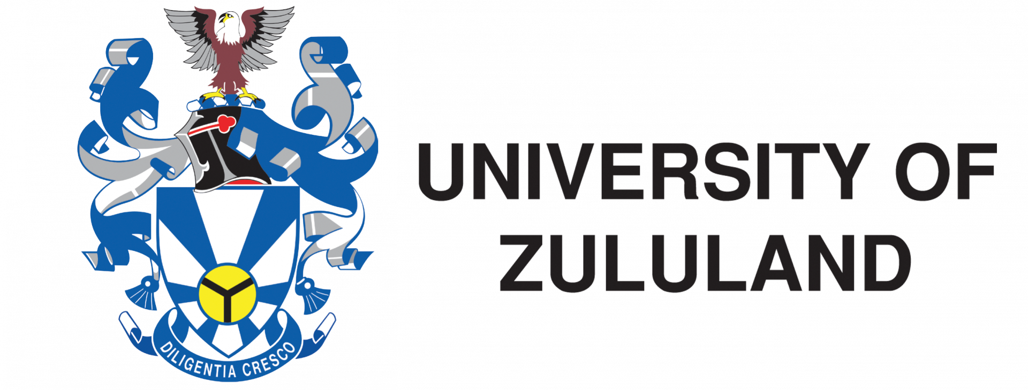
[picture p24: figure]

0.05
0.10
0.20
0.30
0.40
0.60

Wt. % CdS


## Transmittance

Trial#1


## Photoluminescence

Trial#1


## Light Yield

Trial#1


## Problems and Potential Solutions

Trial#1

Low transmittance
Nanoparticle aggregation
Poor polymer integration
Low light yield
Inefficient energy transfer
Inadequate active centers
High self absorption
Surface Ligand Exchange
Co-polymerizable coupling agents
Mitigate defect formation
Conventional dopants
Secondary active centers – PPO
Wavelength shifter - POPOP

## Trial #2 – Conventional Polystyrene

Styrene
2,5-Diphenyloxazole (PPO)
1,4-Bis(5-phenyl-2-oxazolyl)benzene (POPOP)

1,4-Bis(5-phenyl-2-oxazolyl)benzene BioReagent, suitable for scintillation

## Trial #2 – Conventional Polystyrene


Styrene
PPO
POPOP


## Energy spectrum

Trial#2


## Trial #3 – Add CdSe nanoparticles

## Thank you!

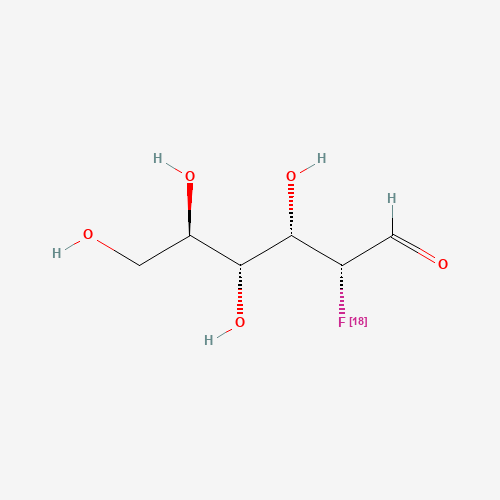
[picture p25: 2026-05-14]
Figures/Theory/Fludeoxyglucose F-18.png

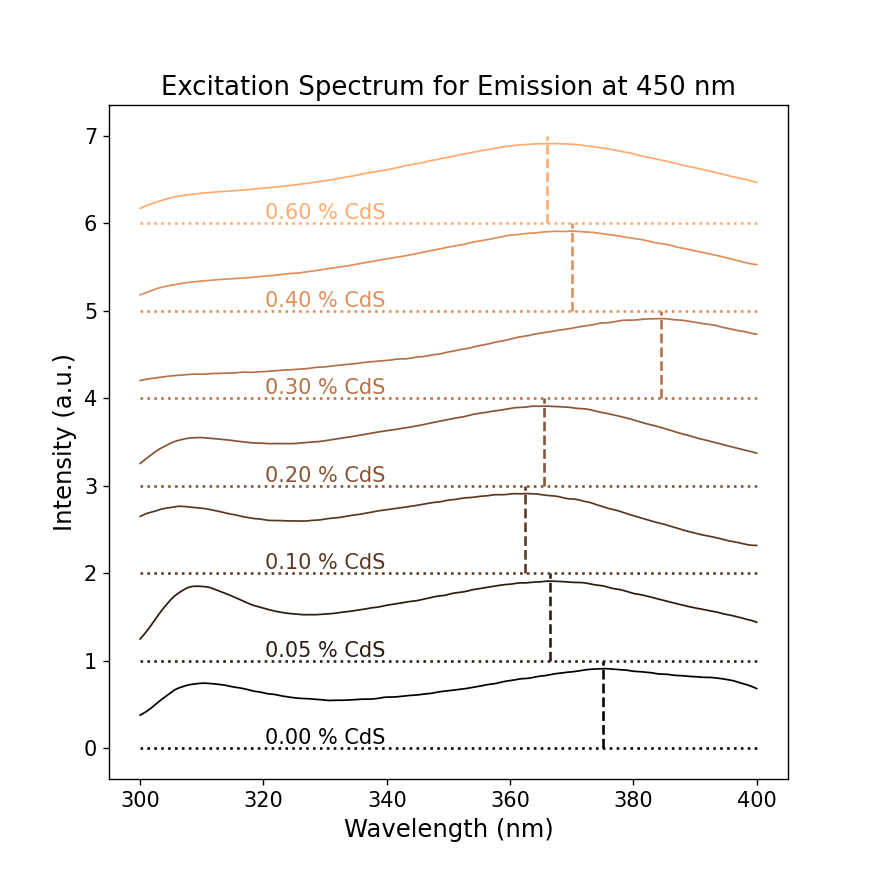
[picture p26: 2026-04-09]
Figures/Photoluminescence/ex_for_em450.png

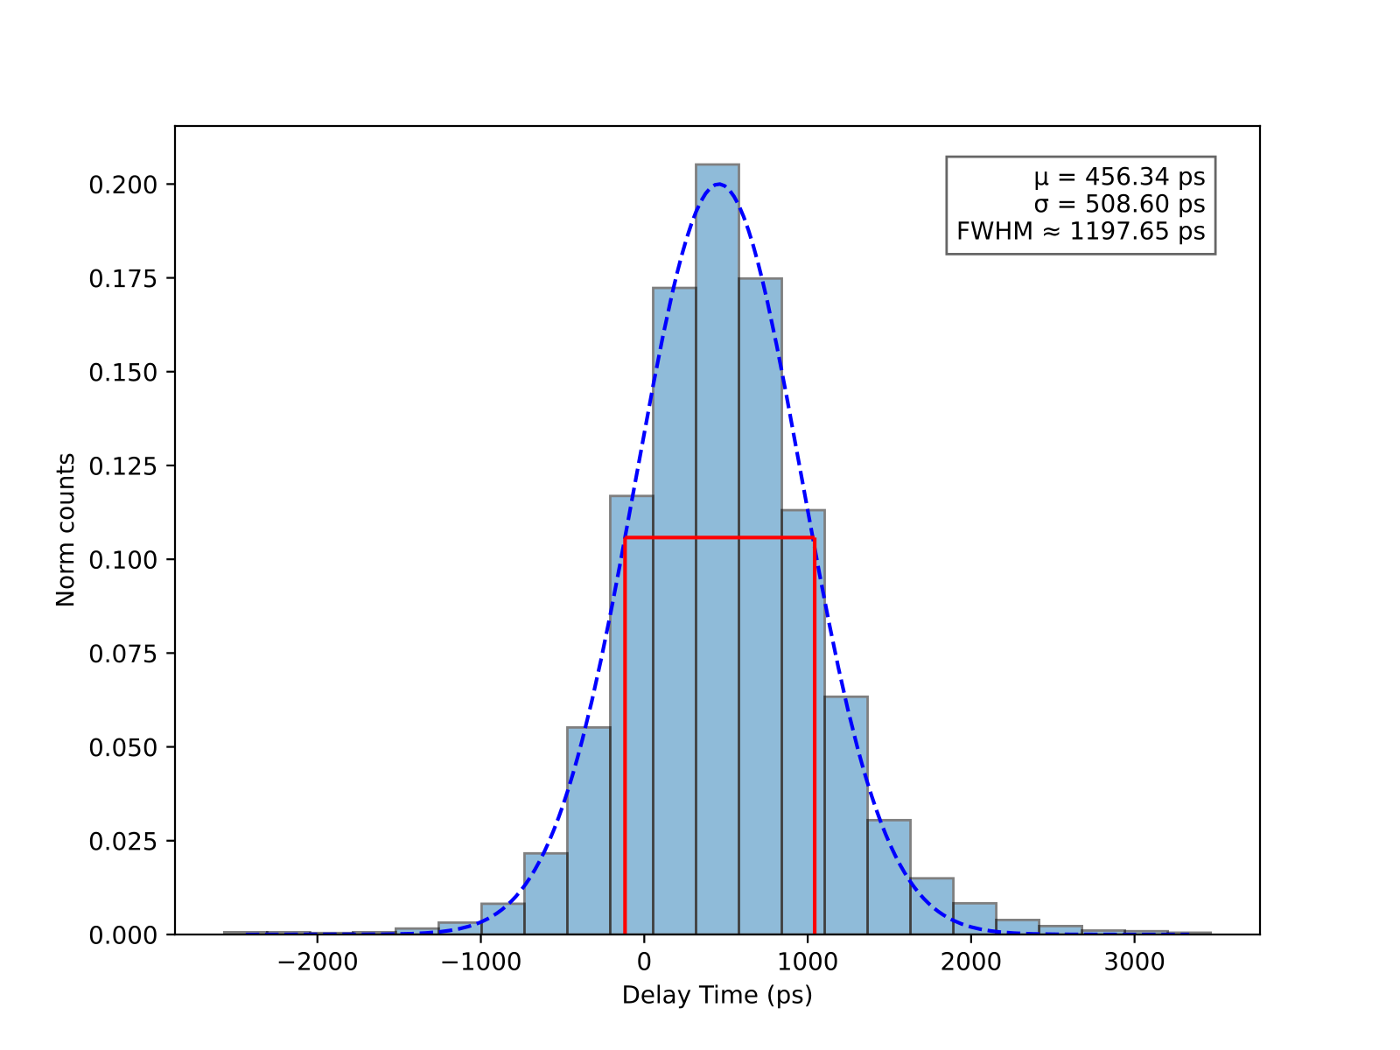
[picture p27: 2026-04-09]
Figures/CTR/UCT_LYSO_LYSO_CTR.png

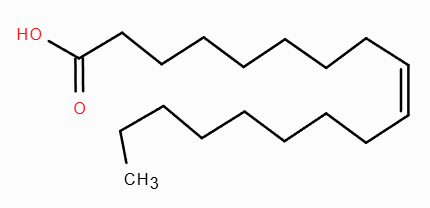
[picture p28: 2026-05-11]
oleic_acid_structure.png

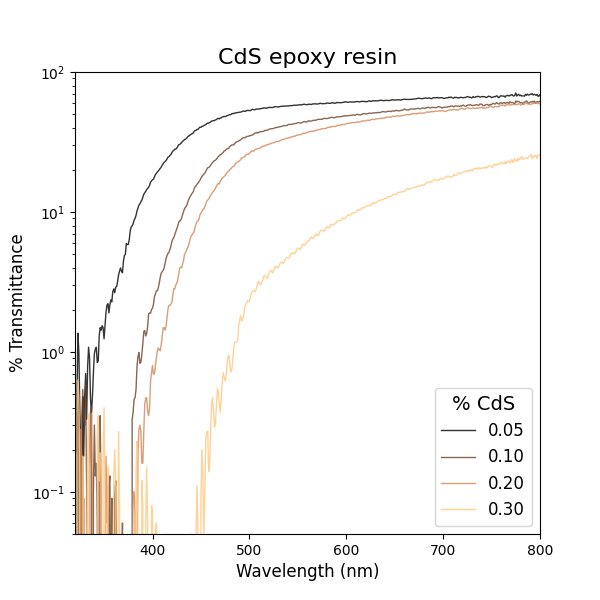
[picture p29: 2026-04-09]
Figures/Transmittance/cds_a_log.png

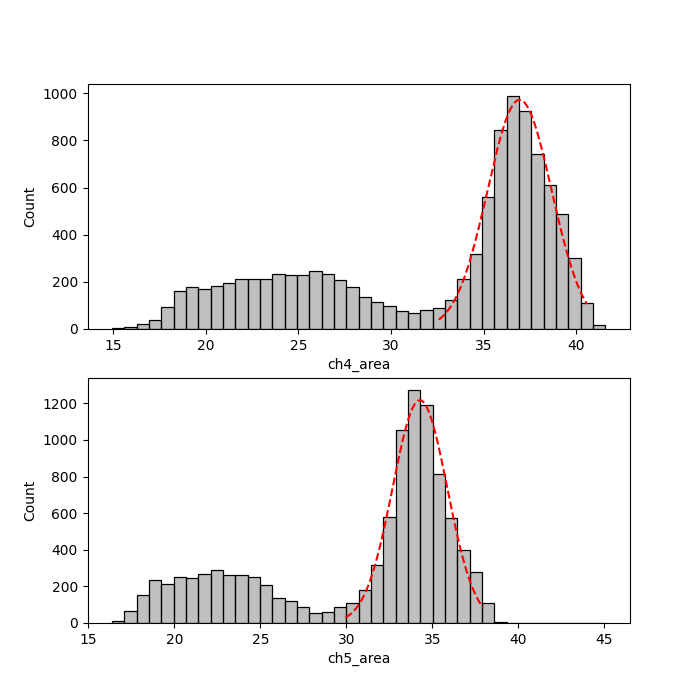
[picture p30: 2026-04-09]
Figures/CTR/LYSO_LYSO_energy.png

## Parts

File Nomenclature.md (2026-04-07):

The following list of relevant metrics is found at the end of ***Bright Innovations*** review.
# Stopping Power
- The efficiency with which a material absorbs ionizing radiation of a specific type and energy.
- Enhanced by increasing atomic number (Z)
# Light Yield
- The number of scintillation photons emitted as a direct result of the energy of incident radiation
- **Physical LY**  is intrinsic to the material and is the number of photons generated by the material.
- **Technical LY** is the number of photons that make it out of the material, determined by the efficiency of light transport post-scintillation. It is deteriorated by self-absorption, scattering and internal reflection.
# Rise Time 
- Characteristic time defining leading each of a scintillation pulse.
- Shaped by excitation dynamics associated with transfer to emission states.
# Decay Time
- Characteristic time(s) of one (or more) scintillation components.
- Depends on kinetics of charge carrier transport to scintillating centers and the internal luminescence of such centers.
- Affects distinguishability between individual pulses and ultimately detector time resolution
# Time Resolution
- The precision with which the exact instant of radiation event detection can be identified.
- Influenced by both the rise and decay times, and the light yield - approximately given by $$ R \approx \sqrt{\frac{\tau_r\cdot\tau_d}{LY}}$$
- Faster response times and higher LYs are advantageous for good time resolution
# Coincidence Time Resolution (CTR)
- The time resolution of two detectors when detecting simultaneous scintillation events.
# Energy Resolution
- Full-width half maximum of energy peak divided by the energy associated with that peak. 
## Photoelectric cross section
- The efficiency of the photoelectric interaction in a material.
- Dependent on type and energy of incident radiation, as well as the intrinsic properties of the material. 
# Transmittance
- The relative intensity of light leaving a material with respect to the incident intensity $$T=\frac{I_{out}}{I_{in}}$$
- Usually given as a function of wavelength.
# Absorbance
- The inverse of [transmittance](#transmittance) - literally $$A=T^{-1}$$
- Also usually given as a function of wavelength.
# Stokes shift
- The difference between excitation and emission wavelength.
# Self-absorption
- The extent to which a material re-absorbs the photons it emits.
# SiPM
- Silicon Photomultiplier used to generate an electronic signal from incident photons. 
# Matrix
%% To do %%
# Wavelength shifter
%% To do %%
## FRET
- Fluorescent (Forster) Resonant Energy Transfer
- Radiative transfer of energy from higher to lower energy (frequency) photon emission.
## DET
- Dexter Energy Transfer
- Non-radiative transfer of energy from gamma interaction centers to scintillation centers, usually via a photoelectron or phonons.

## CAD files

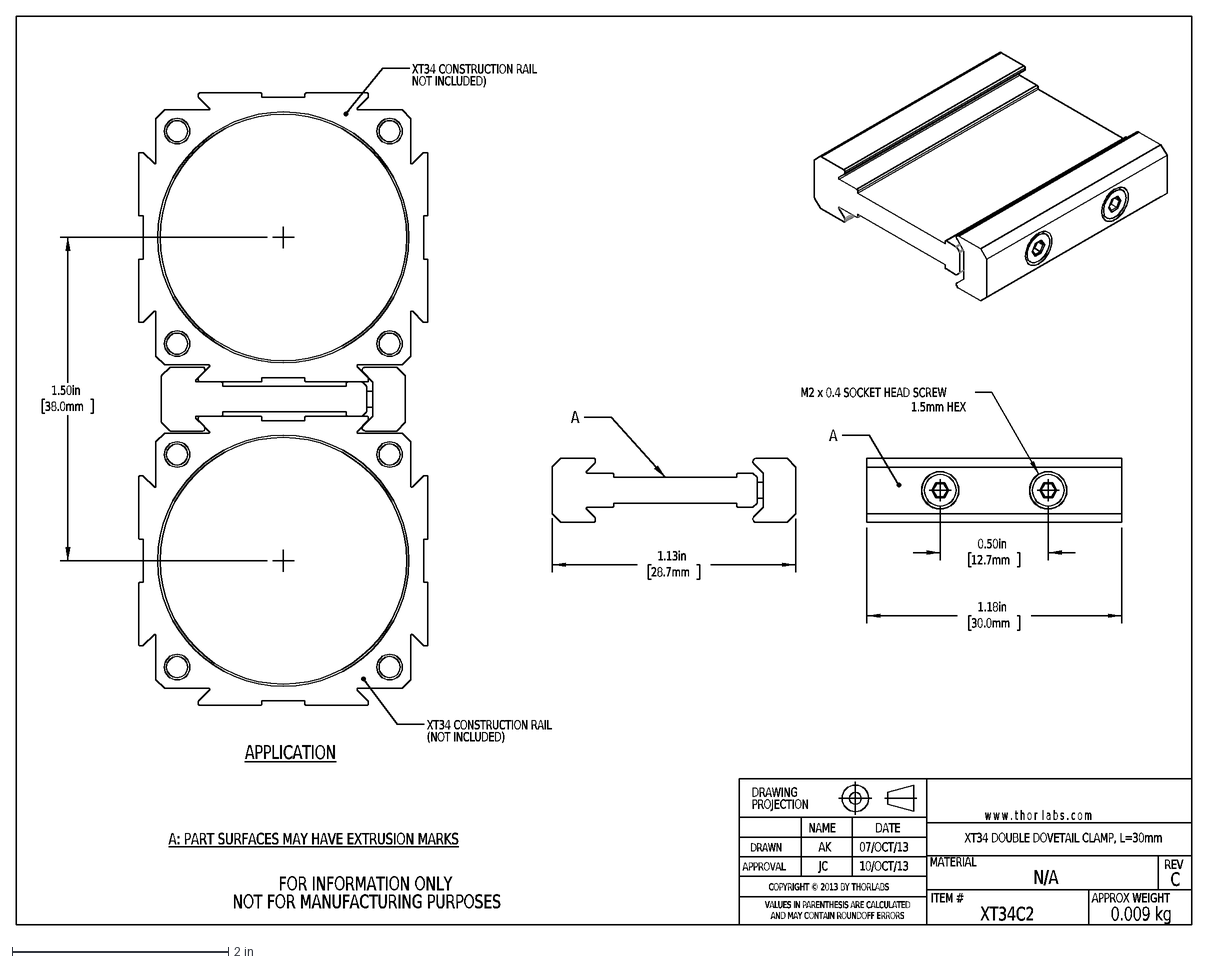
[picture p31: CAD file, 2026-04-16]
Apparatus/CTR Bench/Mechanics/DXF/XT34C2-AutoCADDXF.dxf
A: PART SURFACES MAY HAVE EXTRUSION MARKS
C
XT34C2
MATERIAL
DRAWN
APPROVAL
REV
AK
JC
07/OCT/13
DATE
10/OCT/13
w w w . t h o r l a b s . c o m
ITEM #
APPROX WEIGHT
N/A
0.009 kg
VALUES IN PARENTHESIS ARE CALCULATED
AND MAY CONTAIN ROUNDOFF ERRORS
DRAWING
PROJECTION
NAME
FOR INFORMATION ONLY
NOT FOR MANUFACTURING PURPOSES
XT34 DOUBLE DOVETAIL CLAMP, L=30mm
COPYRIGHT © 2013 BY THORLABS
1.13in
28.7mm
A
1.18in
30.0mm
0.50in
12.7mm
M2 x 0.4 SOCKET HEAD SCREW
1.5mm HEX
1.50in
38.0mm
APPLICATION
XT34 CONSTRUCTION RAIL
NOT INCLUDED)
(NOT INCLUDED)

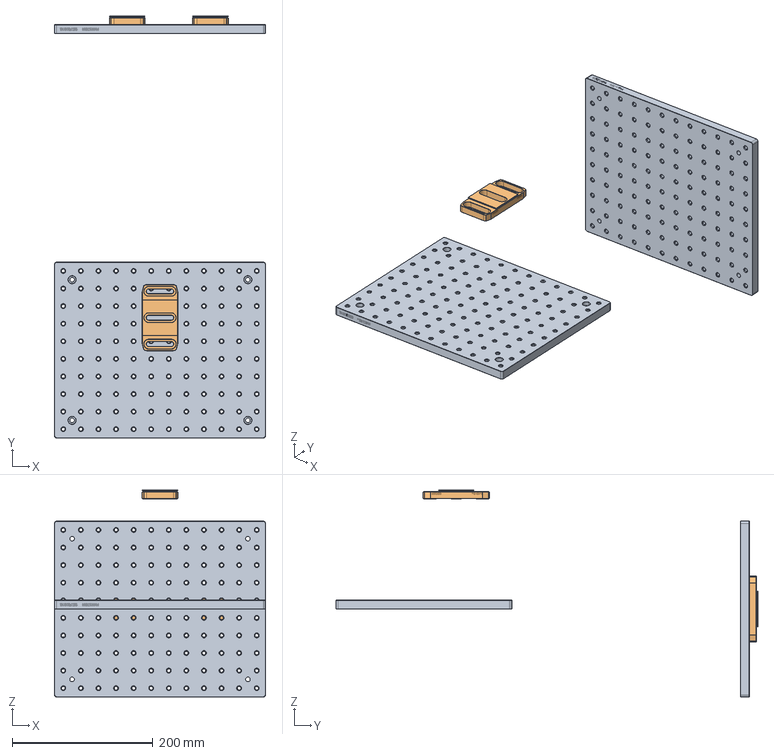
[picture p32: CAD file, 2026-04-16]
Apparatus/CTR Bench/Mechanics/Minimal.FCStd
300.0 x 599.9 x 294.2 mm
MB2530_M x 2
TTN126443-E0W x 3

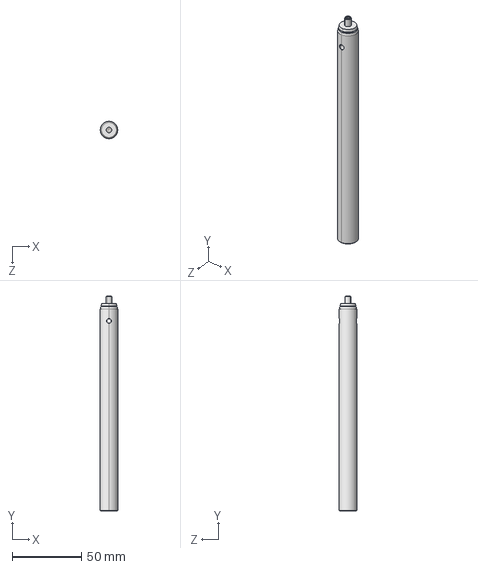
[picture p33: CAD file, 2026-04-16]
Apparatus/CTR Bench/Mechanics/STEP/TR150_M-Step.step
12.7 x 155.3 x 12.7 mm

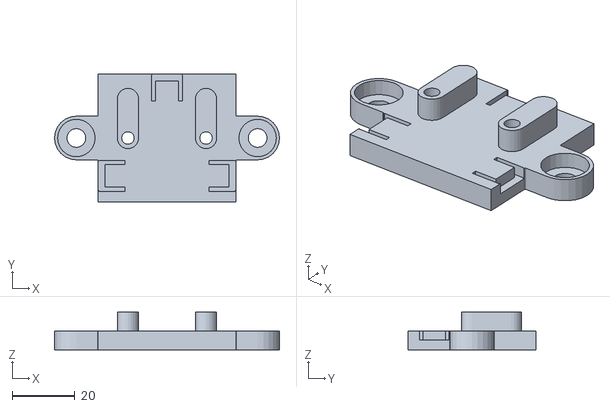
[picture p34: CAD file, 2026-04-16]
Apparatus/CTR Bench/PCB Mount/3D Print/MountBottom.stl
72.0 x 41.0 x 12.0

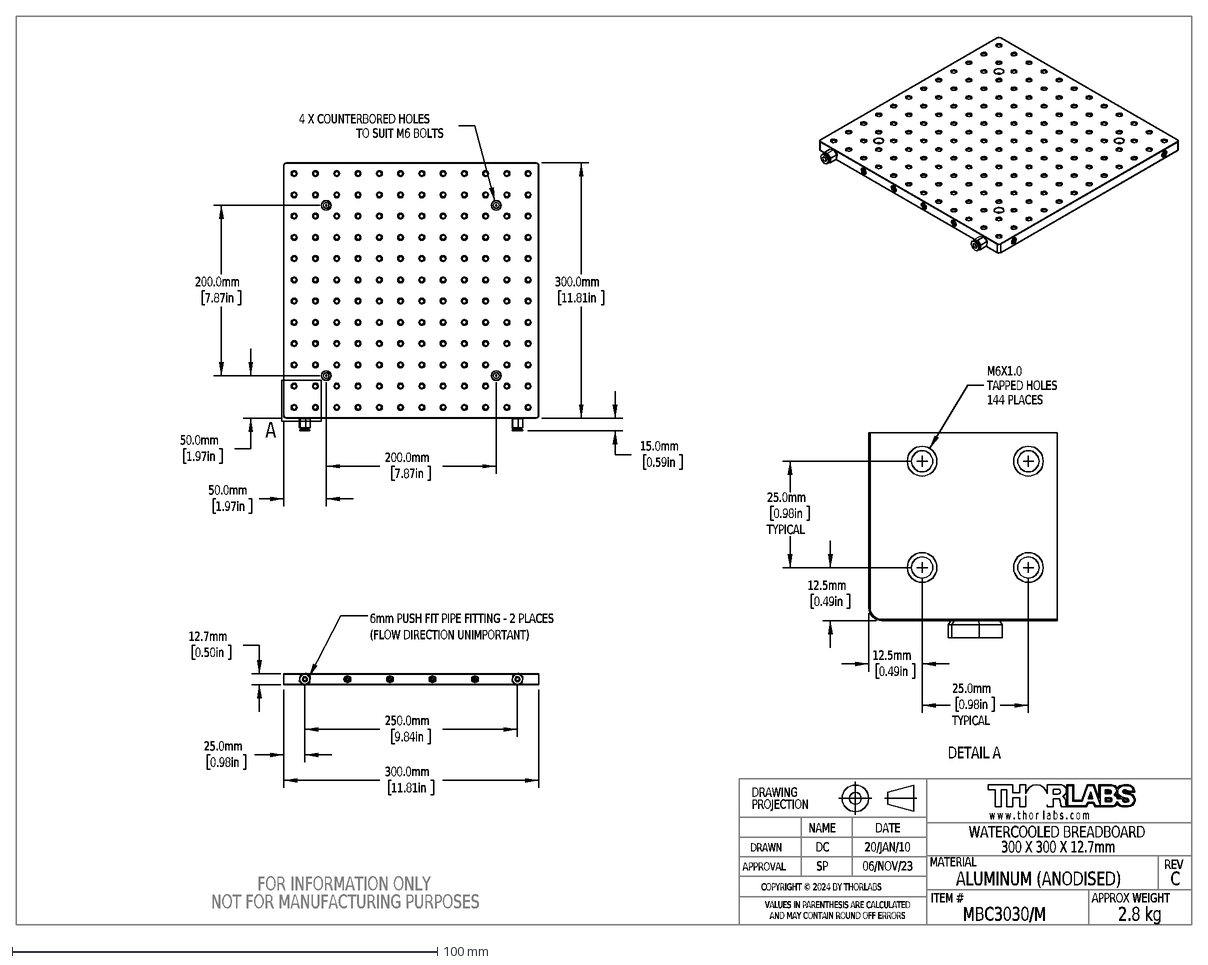
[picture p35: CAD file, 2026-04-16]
Apparatus/CTR Bench/Mechanics/DXF/MBC3030_M-AutoCADDXF.dxf
MATERIAL
DRAWN
APPROVAL
REV
DATE
w w w . t h o r l a b s . c o m
ITEM #
APPROX WEIGHT
VALUES IN PARENTHESIS ARE CALCULATED
AND MAY CONTAIN ROUND OFF ERRORS
DRAWING
PROJECTION
NAME
COPYRIGHT © 2024 BY THORLABS
FOR INFORMATION ONLY
NOT FOR MANUFACTURING PURPOSES
MBC3030/M
2.8 kg
C
WATERCOOLED BREADBOARD
300 X 300 X 12.7mm
ALUMINUM (ANODISED)
SP
DC
20/JAN/10
06/NOV/23
300.0mm
11.81in
200.0mm
7.87in
50.0mm
1.97in
15.0mm
0.59in
4 X COUNTERBORED HOLES
TO SUIT M6 BOLTS
A
250.0mm
9.84in
25.0mm
0.98in
12.7mm
0.50in
6mm PUSH FIT PIPE FITTING - 2 PLACES
(FLOW DIRECTION UNIMPORTANT)
12.5mm
0.49in
TYPICAL
M6X1.0
TAPPED HOLES
144 PLACES
DETAIL A

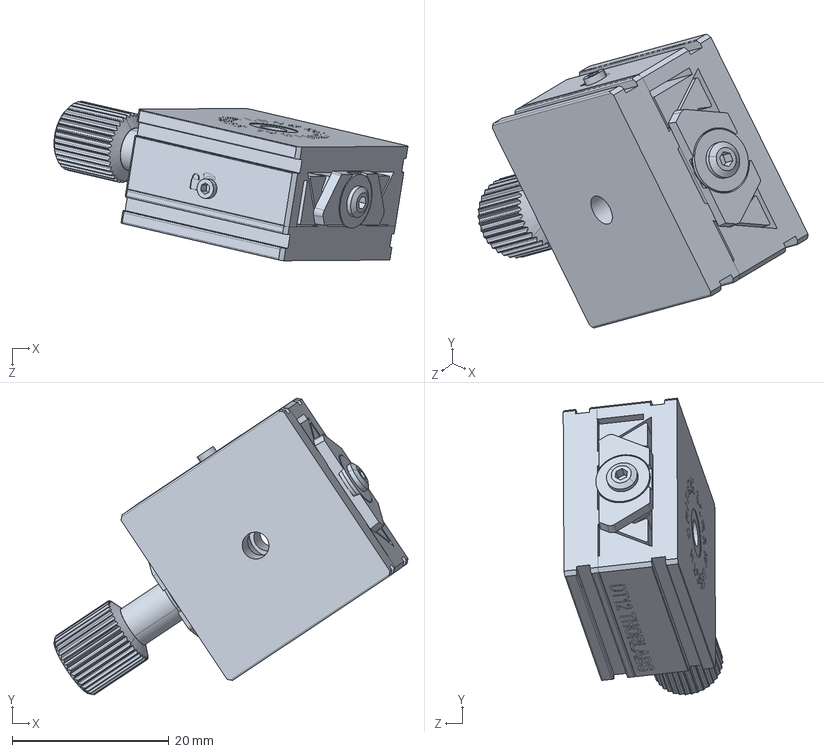
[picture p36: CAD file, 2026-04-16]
Apparatus/CTR Bench/Mechanics/STEP/DT12_M-Step.step
45.1 x 37.8 x 20.4 mm

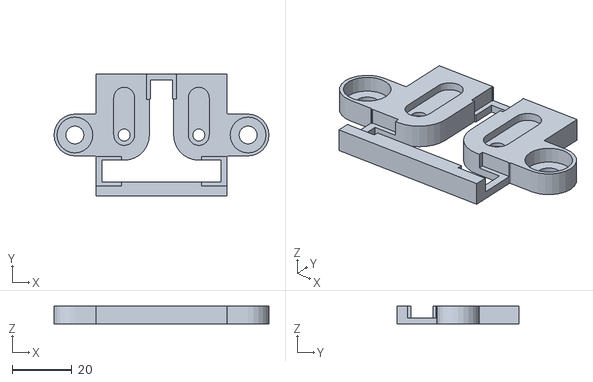
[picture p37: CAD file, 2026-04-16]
Apparatus/CTR Bench/PCB Mount/3D Print/MountTop.stl
72.0 x 41.0 x 6.00

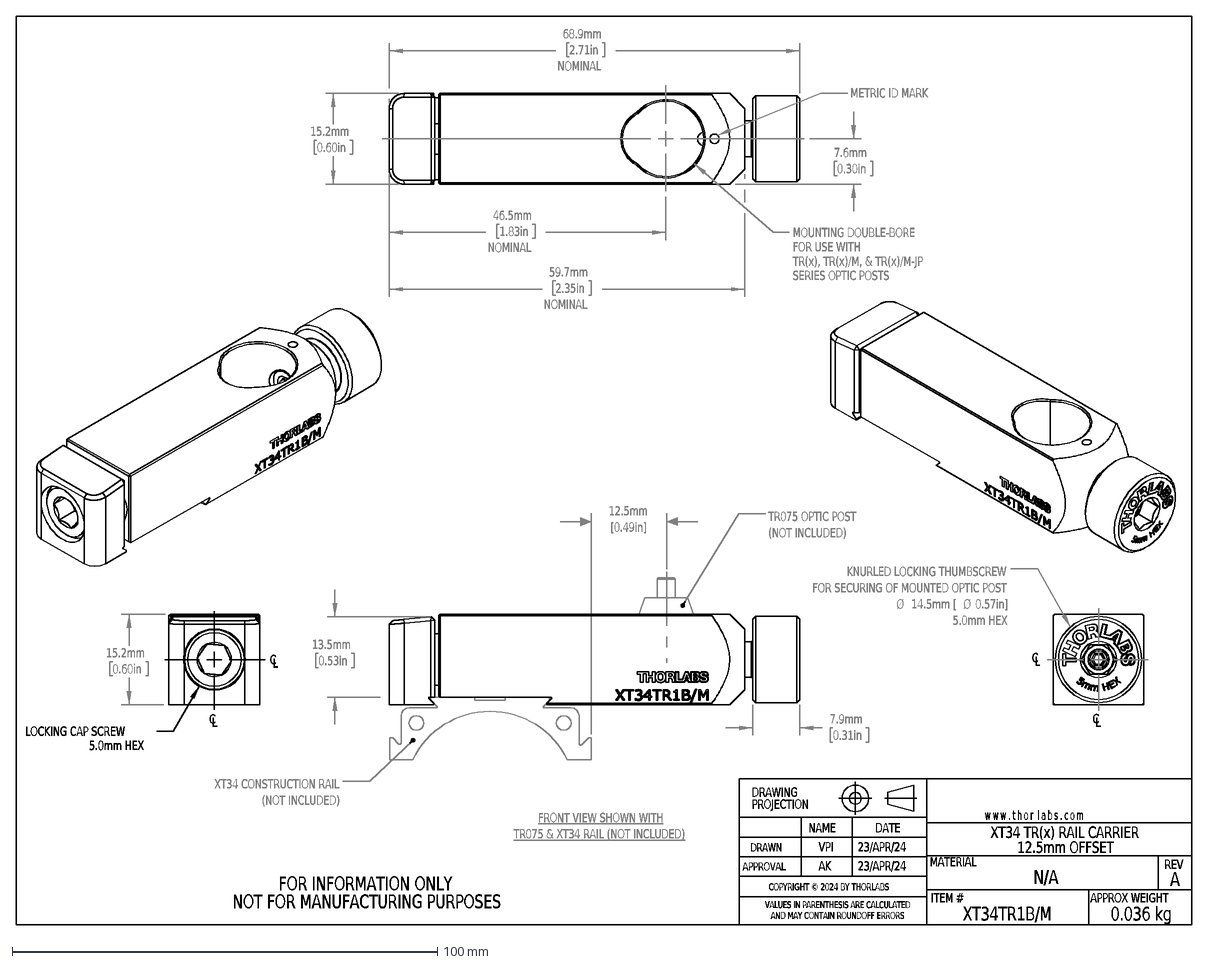
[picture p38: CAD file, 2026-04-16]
Apparatus/CTR Bench/Mechanics/DXF/XT34TR1B_M-AutoCADDXF.dxf
12.5mm
[0.49in]
A
XT34TR1B/M
MATERIAL
DRAWN
APPROVAL
REV
VPI
AK
23/APR/24
DATE
w w w . t h o r l a b s . c o m
ITEM #
N/A
0.036 kg
VALUES IN PARENTHESIS ARE CALCULATED
AND MAY CONTAIN ROUNDOFF ERRORS
DRAWING
PROJECTION
NAME
FOR INFORMATION ONLY
NOT FOR MANUFACTURING PURPOSES
XT34 TR(x) RAIL CARRIER
12.5mm OFFSET
COPYRIGHT © 2024 BY THORLABS
APPROX WEIGHT
7.9mm
0.31in
13.5mm
0.53in
XT34 CONSTRUCTION RAIL
(NOT INCLUDED)
TR075 OPTIC POST
FRONT VIEW SHOWN WITH
TR075 & XT34 RAIL (NOT INCLUDED)
15.2mm
0.60in
LOCKING CAP SCREW
5.0mm HEX
C
L
KNURLED LOCKING THUMBSCREW
FOR SECURING OF MOUNTED OPTIC POST
Ø
14.5mm [
0.57in]
MOUNTING DOUBLE-BORE
FOR USE WITH
TR(x), TR(x)/M, & TR(x)/M-JP
SERIES OPTIC POSTS
7.6mm
0.30in
59.7mm
2.35in
NOMINAL
46.5mm
1.83in
68.9mm
2.71in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

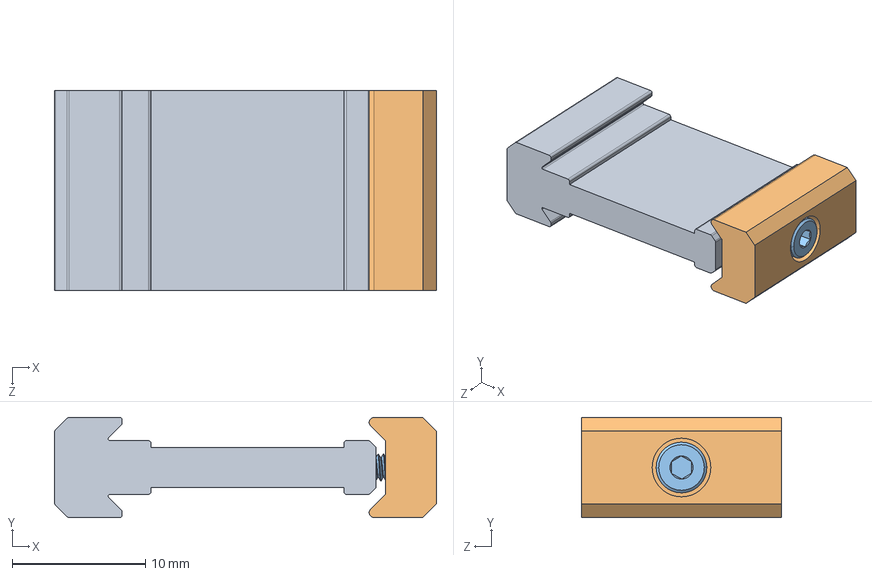
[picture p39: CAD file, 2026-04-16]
Apparatus/CTR Bench/Mechanics/STEP/XT34C1-Step.step
28.7 x 7.52 x 15.0 mm

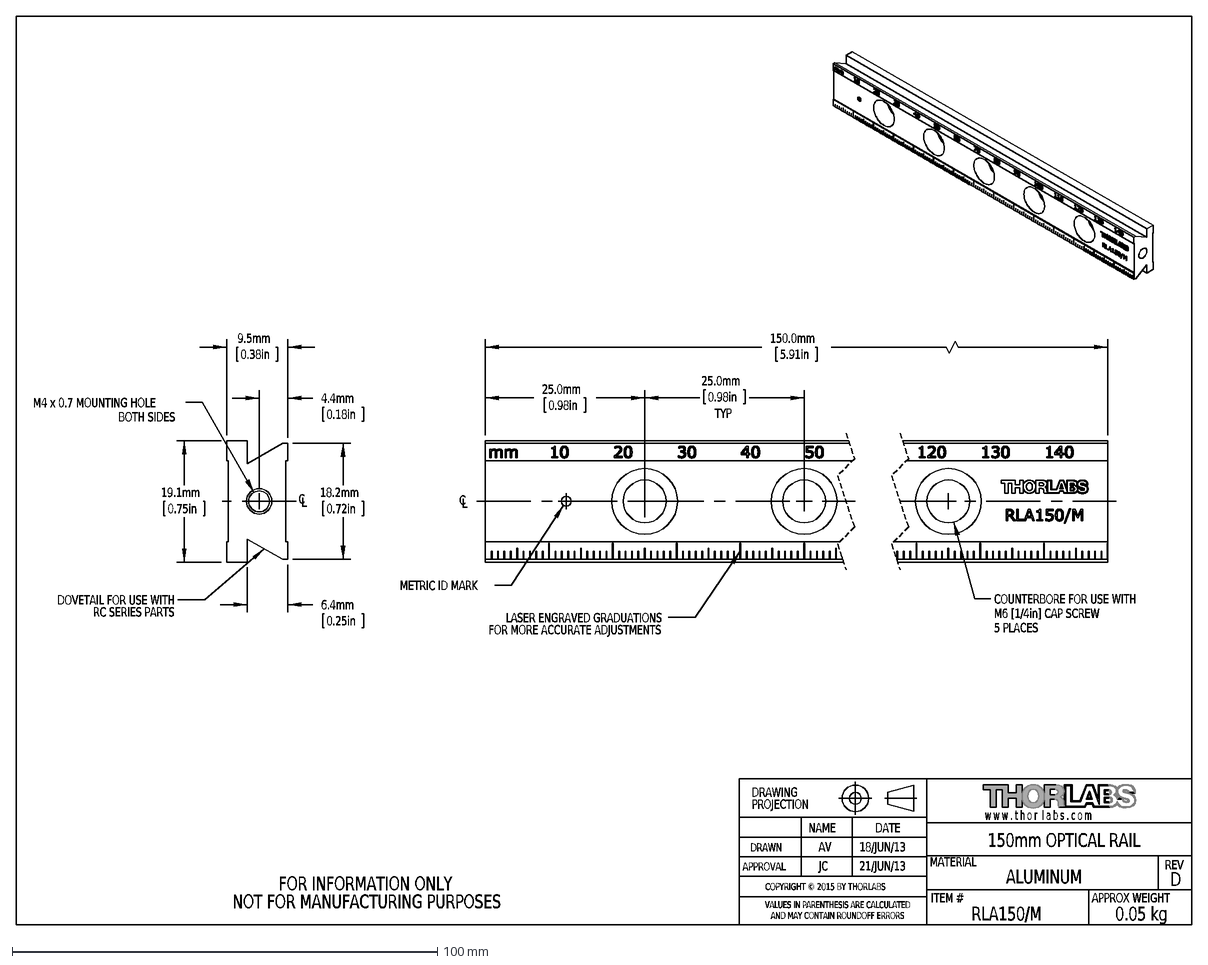
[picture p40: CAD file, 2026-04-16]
Apparatus/CTR Bench/Mechanics/DXF/RLA150_M-AutoCADDXF.dxf
D
RLA150/M
MATERIAL
DRAWN
APPROVAL
REV
AV
JC
18/JUN/13
DATE
21/JUN/13
w w w . t h o r l a b s . c o m
ITEM #
APPROX WEIGHT
ALUMINUM
0.05 kg
VALUES IN PARENTHESIS ARE CALCULATED
AND MAY CONTAIN ROUNDOFF ERRORS
DRAWING
PROJECTION
NAME
FOR INFORMATION ONLY
NOT FOR MANUFACTURING PURPOSES
150mm OPTICAL RAIL
COPYRIGHT © 2015 BY THORLABS
25.0mm
0.98in
150.0mm
5.91in
TYP
METRIC ID MARK
COUNTERBORE FOR USE WITH
M6 [1/4in] CAP SCREW
5 PLACES
LASER ENGRAVED GRADUATIONS
FOR MORE ACCURATE ADJUSTMENTS
C
L
18.2mm
0.72in
9.5mm
0.38in
4.4mm
0.18in
6.4mm
0.25in
19.1mm
0.75in
M4 x 0.7 MOUNTING HOLE
BOTH SIDES
DOVETAIL FOR USE WITH
RC SERIES PARTS

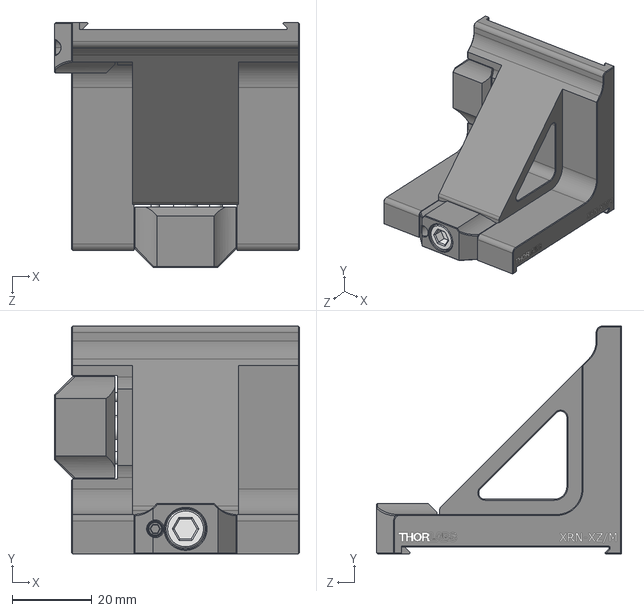
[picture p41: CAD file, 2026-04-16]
Apparatus/CTR Bench/Mechanics/STEP/XRN-XZ_M-StepBracket.step
61.4 x 57.2 x 61.4 mm

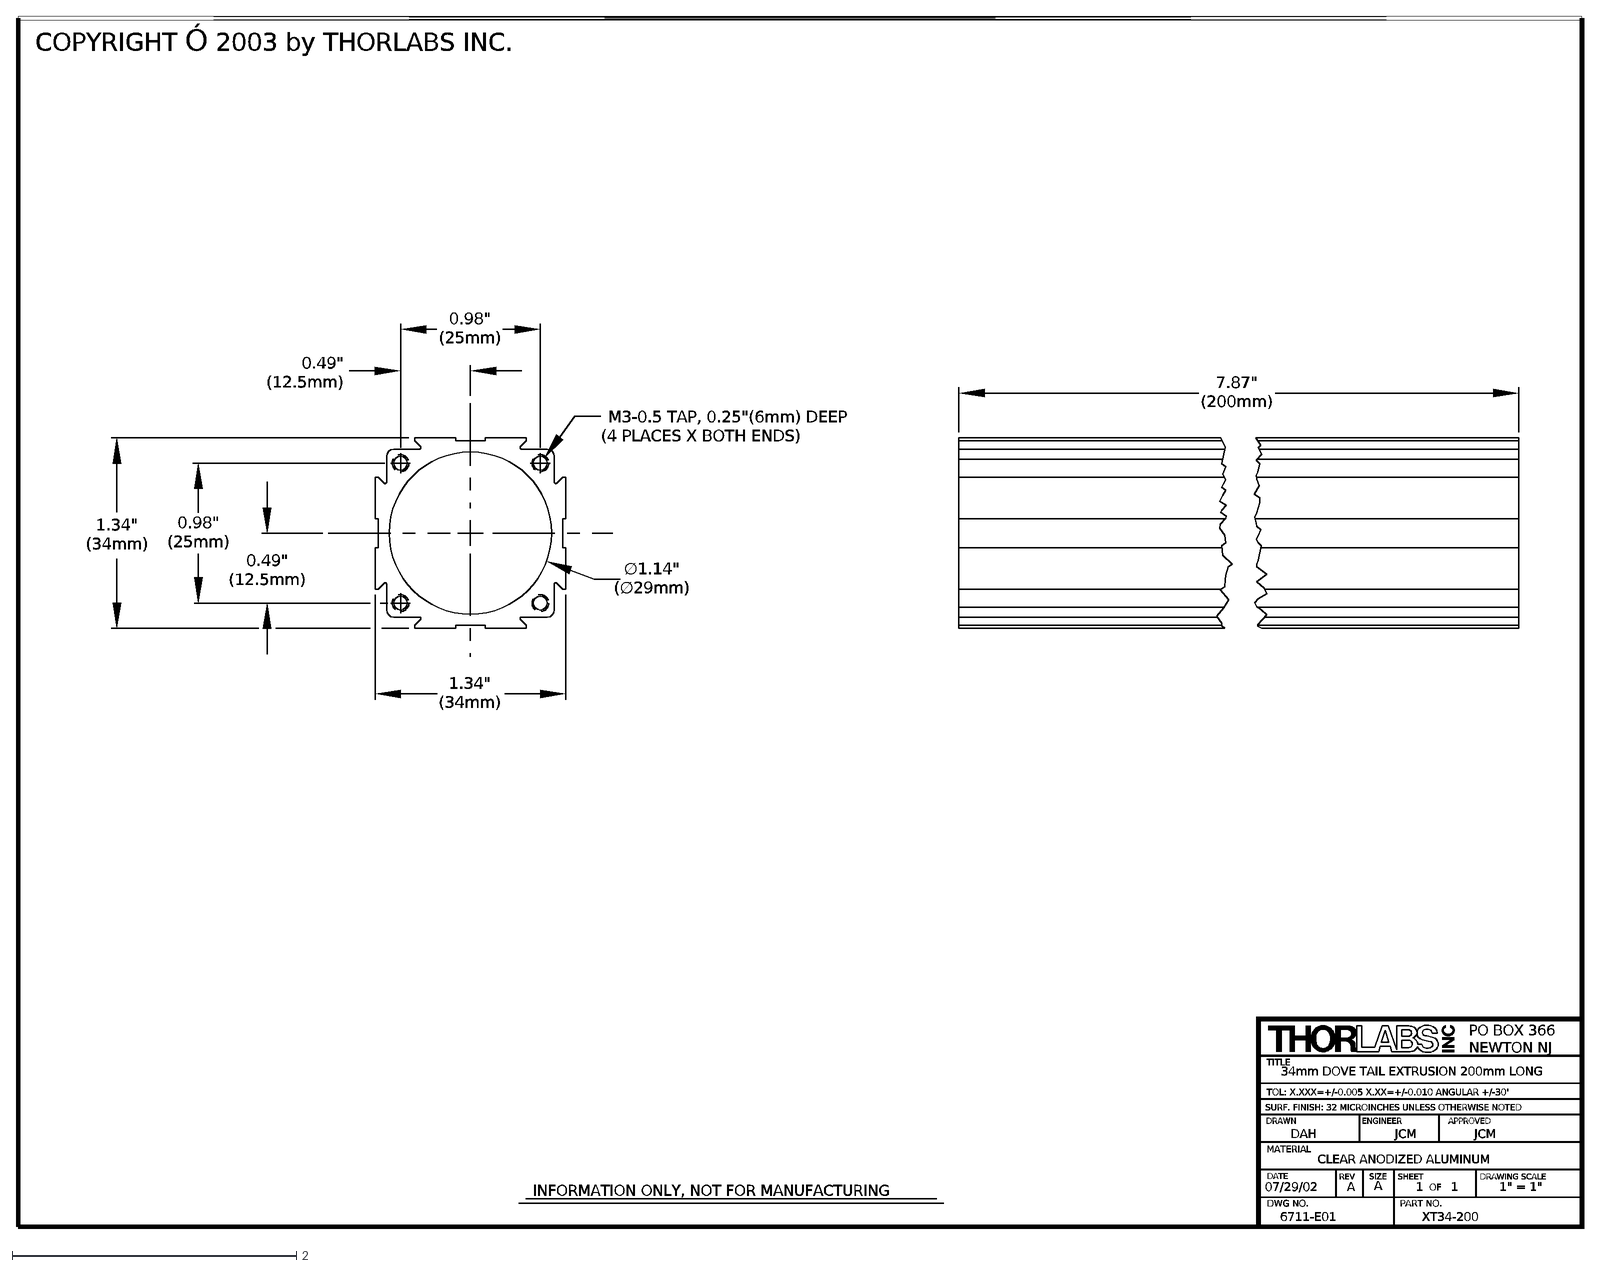
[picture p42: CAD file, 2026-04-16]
Apparatus/CTR Bench/Mechanics/DXF/XT34-200-AutoCADDXF.dxf
SURF. FINISH: 32 MICROINCHES UNLESS OTHERWISE NOTED
CLEAR ANODIZED ALUMINUM
34mm DOVE TAIL EXTRUSION 200mm LONG
TOL: X.XXX=+/-0.005 X.XX=+/-0.010 ANGULAR +/-30'
6711-E01
07/29/02
DAH
DWG NO.
MATERIAL
DATE
TITLE
DRAWN
XT34-200
A
SIZE
JCM
1
APPROVED
PART NO.
REV
SHEET
OF
ENGINEER
NEWTON NJ
PO BOX 366
DRAWING SCALE
1" = 1"
7.87" (200mm)
M3-0.5 TAP, 0.25"(6mm) DEEP
(4 PLACES X BOTH ENDS)
1.34" (34mm)
0.49" (12.5mm)
0.98" (25mm)
INFORMATION ONLY, NOT FOR MANUFACTURING
∅1.14" (∅29mm)

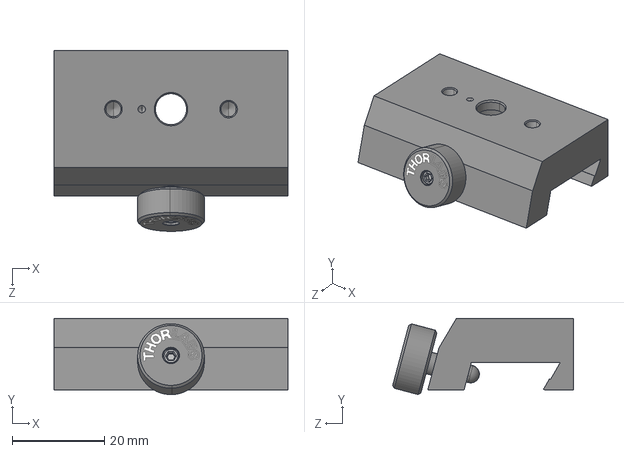
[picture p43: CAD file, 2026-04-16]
Apparatus/CTR Bench/Mechanics/STEP/RC2_M-Step.step
50.8 x 16.5 x 39.2 mm

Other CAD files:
Apparatus/CTR Bench/PCB Mount/MicroFC SMA board.dwg
Apparatus/CTR Bench/PCB Mount/MountSidePrint.dwg
Apparatus/CTR Bench/PCB Mount/PCB.dwg
Apparatus/CTR Bench/PCB Mount/slider.dwg
Apparatus/CTR Bench/PCB Mount/MountFootprint.dwg
Apparatus/CTR Bench/Mechanics/DXF/DT12XY_M-AutoCADDXF.dxf
Apparatus/CTR Bench/Mechanics/DXF/DT12XZ_M-AutoCADDXF.dxf
Apparatus/CTR Bench/Mechanics/DXF/LX20_M-AutoCADDXF.dxf
Apparatus/CTR Bench/Mechanics/DXF/MB2530_M-AutoCADDXF.dxf
Apparatus/CTR Bench/Mechanics/DXF/MB3030_M-AutoCADDXF.dxf
Apparatus/CTR Bench/Mechanics/DXF/PH100E_M-AutoCADDXF.dxf
Apparatus/CTR Bench/Mechanics/DXF/PH150E_M-AutoCADDXF.dxf
Apparatus/CTR Bench/Mechanics/DXF/PH75E_M-AutoCADDXF.dxf
Apparatus/CTR Bench/Mechanics/DXF/RC2_M-AutoCADDXF.dxf
Apparatus/CTR Bench/Mechanics/DXF/RLA075_M-AutoCADDXF.dxf
Apparatus/CTR Bench/Mechanics/DXF/RLA300_M-AutoCADDXF.dxf
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

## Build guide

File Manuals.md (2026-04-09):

# Oscilloscope
The primary instrument used for characterization is the Tektronix Series 6 Mixed Signal Oscilloscope.
- [4-5-6_MSO_ProgrammerManual-077189800](Manuals/Oscilloscope/4-5-6_MSO_ProgrammerManual-077189800.pdf) 
- [5_series](Manuals/Oscilloscope/5_series.pdf)
- [6-Series-B-MSO-Service_077169601](Manuals/Oscilloscope/6-Series-B-MSO-Service_077169601.pdf)
- [MSO4-MSO5-MSO58LP-MSO6-Printable-Help-077130311](Manuals/Oscilloscope/MSO4-MSO5-MSO58LP-MSO6-Printable-Help-077130311.pdf)
# Safety Data Sheets
- [BPO](Manuals/Safety Data Sheets/BPO_SDS.pdf)
- [POPOP](Manuals/Safety Data Sheets/POPOP_SDS.pdf)
- [PPO](Manuals/Safety Data Sheets/PPO_SDS.pdf)
- [Styrene](Manuals/Safety Data Sheets/Styrene_SDS.pdf)
# Scintillators
- [GAGG](Manuals/Scintillators/datasheet-GAGG.pdf)
- [GGAG](Manuals/Scintillators/datasheet-GGAG.pdf)
- [LYSO](Manuals/Scintillators/DYL_HC_Datasheet-Crystal-Material-Index_Lutetium-Yttrium-Silicate_8.5x11_1121.pdf)
- [EJ-200](Manuals/Scintillators/EJ-200.pdf)
- [EJ-232](Manuals/Scintillators/EJ-232, EJ-232Q - Fast Timing Plastic Scintillator - Eljen Technology.pdf)
# SiPM
- [Micro C series](Manuals/SiPM/MICROC_SERIES_C.pdf)
- [Micro J series](Manuals/SiPM/MICROJ_SERIES_J-1489647.pdf)
# Thermocouple
- [Thermocouple measurement](Manuals/Thermocouple/Guide to thermocouple measurements.pdf)

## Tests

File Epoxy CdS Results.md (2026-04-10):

#results
# Description
- Pixels from [Trial 1](EPOXY_CdSRT_28022025.md) were in general of better quality than those of [Trial 2](EPOXY_CdSRT_03032025.md) - the former were more rigid, while the latter were simply too malleable to polish properly (see the two right-most pixels in the figure below). 
- In both cases, QD agglomeration and bubble formation could be clearly seen. 
- Samples with more toluene shrunk more due to toluene evaporating. This means they required more polishing to achieve a flat, smooth surface finish, ultimately removing more material and resulting in pixels of smaller total volume. Compare the 0.05 wt.% pixel with the 0.3 wt.% pixel in the figure below. 

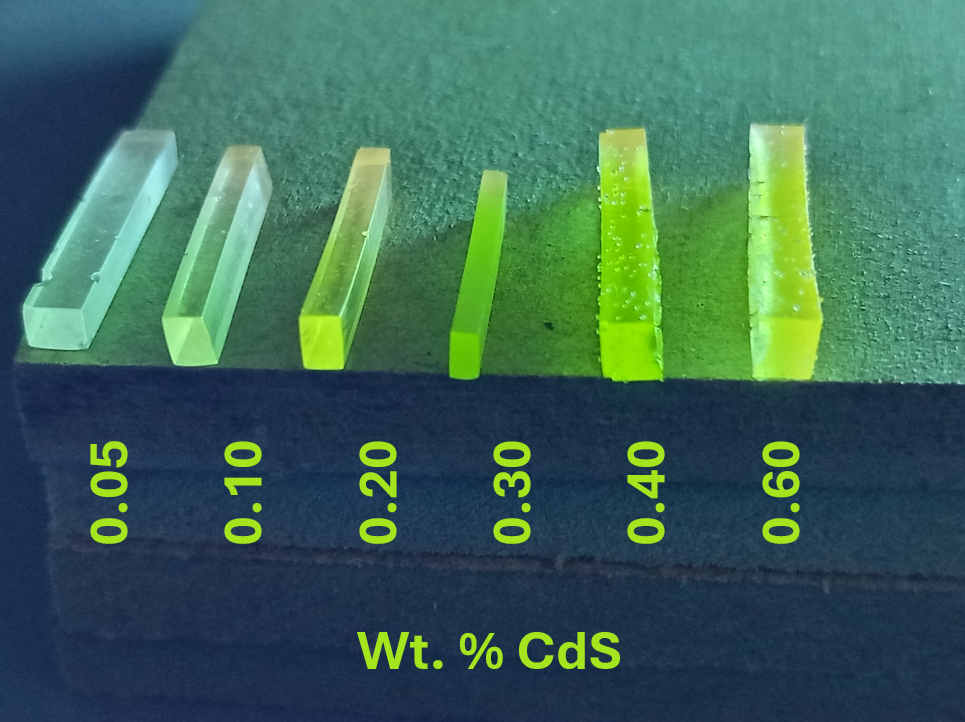
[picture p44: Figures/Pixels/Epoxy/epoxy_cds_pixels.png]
epoxy pixels
 

*Epoxy CdS RT samples under UV illumination*
# Characterization
## Transmittance
Transmittance measurements were made for all samples at the Crystal Clear lab in CERN. The bench directed a variable wavelength light source through samples and into an integrating sphere. A reference beam travelling the same distance through air was used to measure the relative intensity of light passing through the sample.
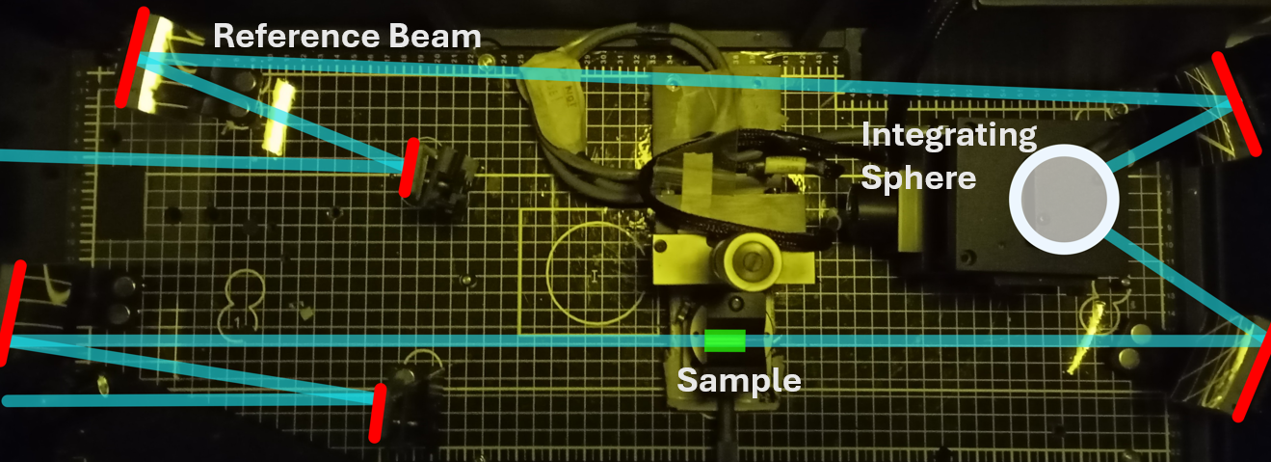
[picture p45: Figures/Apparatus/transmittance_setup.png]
transmittance bench

*Transmittance bench setup at the Crystal Clear lab at CERN*

CdS composite samples were compared with industry standard LYSO, EJ232Q, GAGG (crystal) and GGAG (ceramic) samples. A clear drop in transmittance can be seen with increasing CdS wt.%.

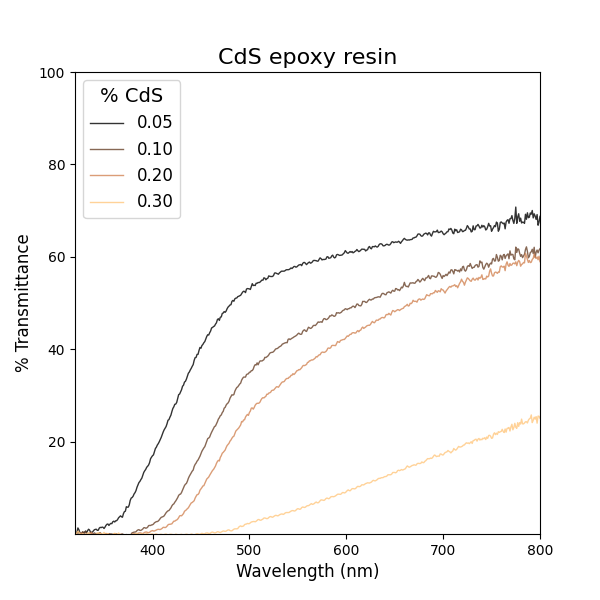
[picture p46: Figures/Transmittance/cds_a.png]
transmittance results


Compare this with the transmittance of the industry standard samples. The "gold standard" is the plastic EJ232Q, while the ceramic GGAG has effectively zero transmittance.

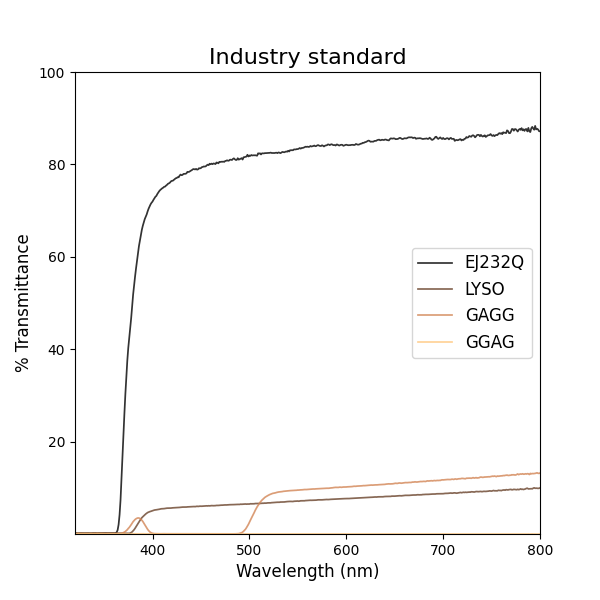
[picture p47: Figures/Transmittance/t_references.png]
transmittance results


*Results of transmission measurements for CdS composite pixels (top) compared to industry standard pixels (bottom).*
## Photoluminescence Spectroscopy
PL measurements were also taken at the Crystal Clear lab at CERN. Pixels were orientated such that the excitation light was incident normal to one face, with the adjacent face normal to the detector (see figure below). This was done to measure PL in transmission mode - essentially to mitigate any direct reflections into the detector. 

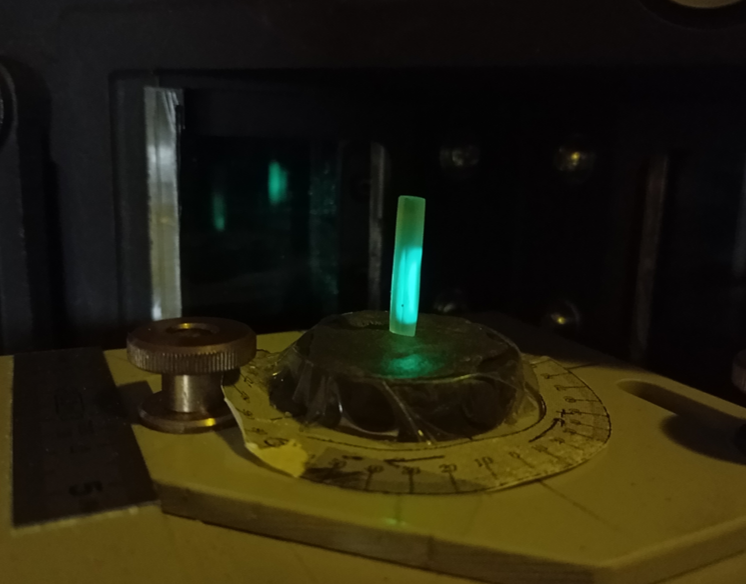
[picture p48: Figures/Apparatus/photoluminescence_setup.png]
pl setup


*Photoluminescence spectroscopy setup at CERN*

Emission spectra have a distinct peak just above 400 nm that shifts to longer wavelengths with increasing QD wt.%. It is worth noting that the highest two wt.% samples were unpolished for this measurement. 
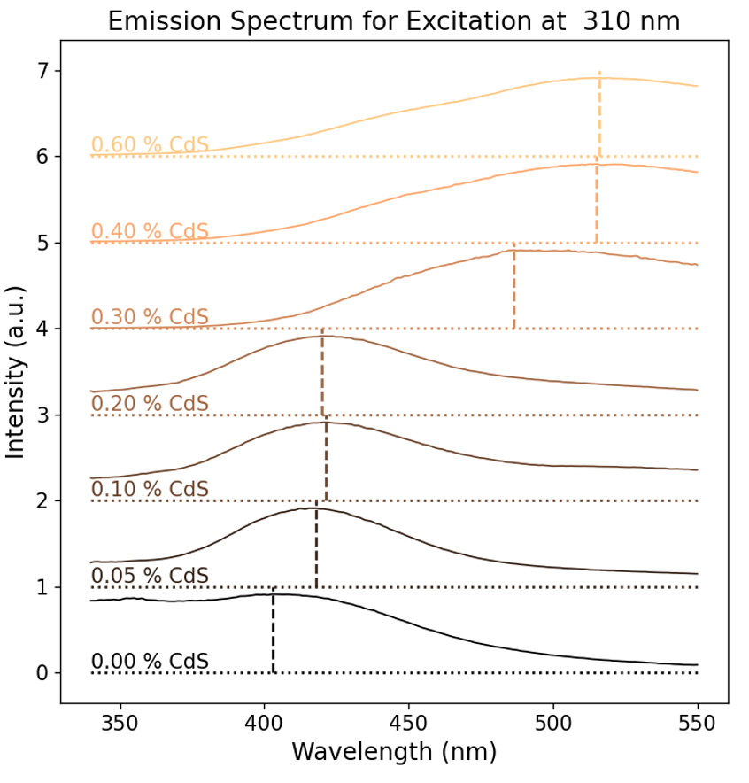
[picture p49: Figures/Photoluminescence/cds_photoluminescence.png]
pl results


*Photoluminescence emission peaks for CdS RT samples under 310 nm excitation.*
## Time Correlated Single Photon Counting
The methodology for this measurement is well described by [Pagano *et al.*](References#pagano2022a)

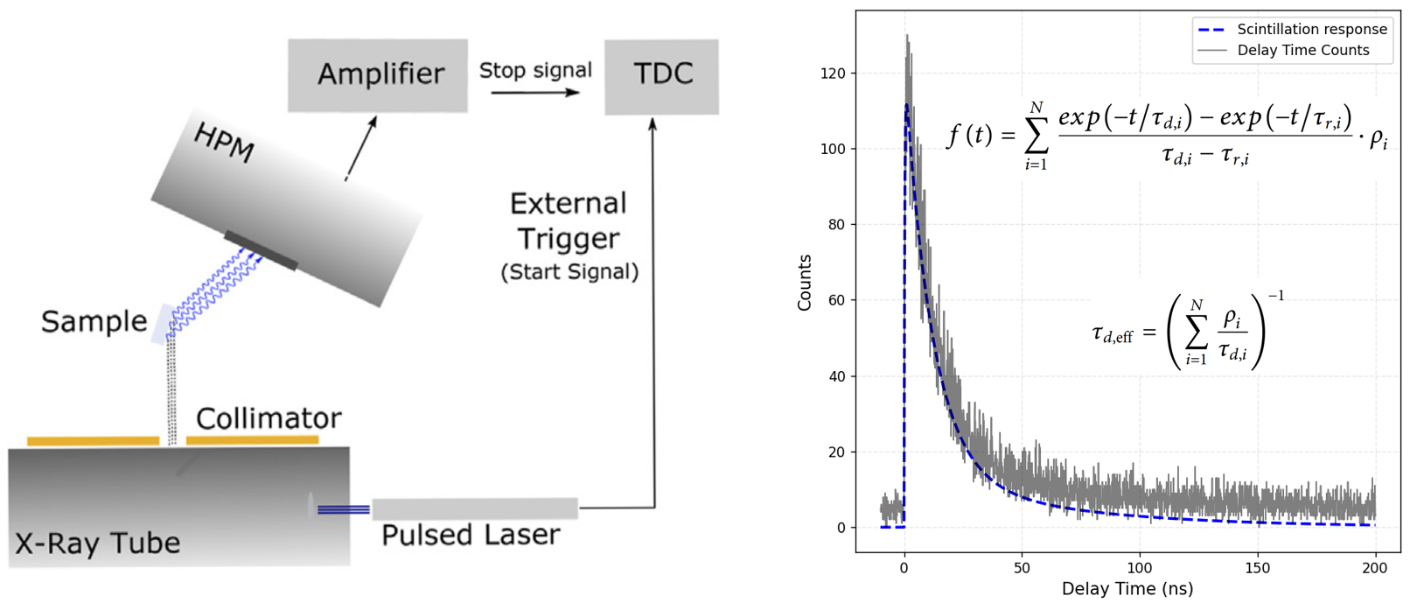
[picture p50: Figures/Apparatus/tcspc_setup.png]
tcsps


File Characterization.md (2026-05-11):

# Optical Properties
## Transmission and Absorbance Spectroscopy
To measure how much light can pass through a pixel as a function of wavelength. [Transmittance](Nomenclature#transmittance) should be maximal at the wavelength of peak detector efficiency. [Absorbance](Nomenclature#absorbance) should be minimal at this same wavelength.
## Photoluminescence Spectroscopy
To measure the peak excitation and emission wavelength, from which the [Stokes shift](Nomenclature#stokes-shift) can be determined. The Stokes shift should be maximized to limit [self-absorption](Nomenclature#self-absorption). 
## Energy Spectrum
Typically a histogram of scintillation pulse integrals over some time window. 
## Energy Resolution
## Coincidence Time Resolution

# Chemical Properties
## Particle Size Distribution
%% To do %%
## Thermogravimetric Analysis
%% To do %%
# Apparatus at UCT
## CTR Bench in the PET Lab
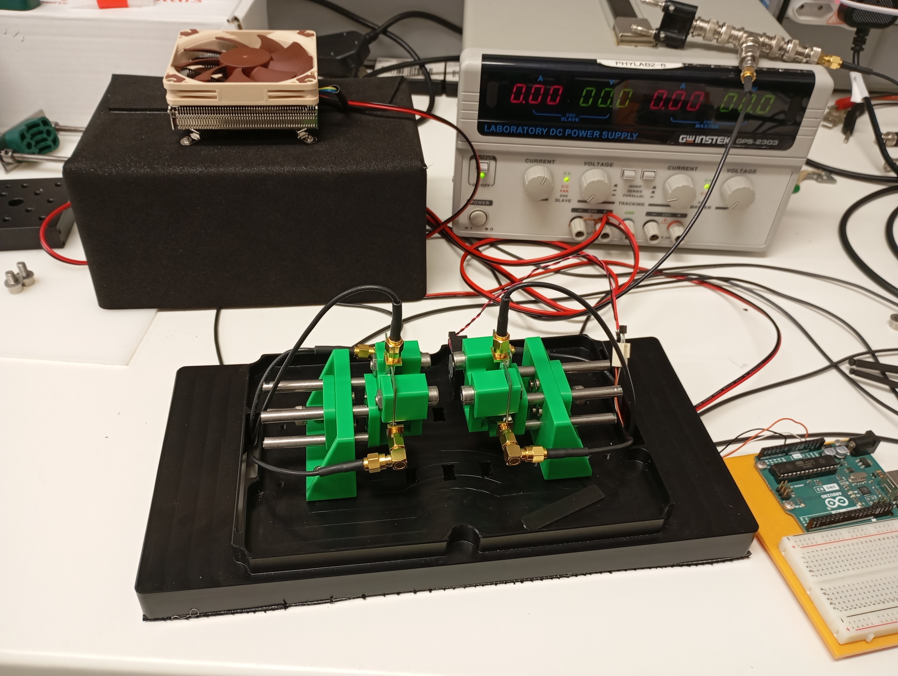
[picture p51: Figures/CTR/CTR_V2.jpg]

## Components
- MICROFJ-SMA-30035-GEVB
- MICROFC-SMA-60035-GEVB
- MICROFC-SMTPA-30050-GEVB
>[!Important] Timing signals *must* be amplified

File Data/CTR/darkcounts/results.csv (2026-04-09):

MEAS1 | MEAS2 | MEAS3 | MEAS4
6.26791651478257e-11 | nan | 0.0002923806619119121 | 0.0035853125
6.40324385604361e-11 | nan | 0.000157176707957958 | 0.003776875
5.8637482446775e-11 | nan | 0.0001728556681681683 | 0.0037503125
6.33908487833333e-11 | nan | 0.000203679617117117 | 0.00356640625
6.2846730927307e-11 | nan | 0.0001621199324324321 | 0.00347734375
6.03875137659757e-11 | nan | 0.0001122516266266267 | 0.00368890625
5.76847938736447e-11 | nan | 5.20683183183185e-05 | 0.0034384375
5.80670501769469e-11 | nan | 0.00214328125 | 0.00352421875
5.9083834488702e-11 | nan | 0.0002220082582582582 | 0.0040178125
5.65646128974739e-11 | 1.26915043506529e-08 | 0.0001817642642642646 | 0.003395

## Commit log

2026-04-09 vault backup: 2026-04-09 09:22:09
    [0_0A.Sample.csv, 2_1A.Sample.csv, 2_1B.Sample.csv, 2_2A.Sample.csv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]
2026-04-09 vault backup: 2026-04-09 13:13:28
    [polystyrene_recipe.xlsx]
2026-04-10 vault backup: 2026-04-10 08:30:30
    [polystyrene_recipe.xlsx]
2026-04-16 vault backup: 2026-04-16 10:36:58
    [132414.dxf, 132414.stp, A2.csv, A4.csv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]
2026-05-11 vault backup: 2026-05-11 17:34:56
    [CdS 10 s (emission 384 nm) (uv 278 nm)-Ex spectra.csv, CdS 10 s emission nm (uv 255 nm).csv, CdS 10 s emission nm (uv 278 nm).csv, CdS 10 s emmision (uv 278 nm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]
2026-05-19 vault backup: 2026-05-19 18:16:06
    [CdSe trial.csv]
2026-06-05 vault backup: 2026-06-05 11:55:20
    [cs lyso 6x6.csv, cs137 ej232 400uVtr 26Vb 60min.csv, cs137 ps 400uVtr 26Vb 60min.csv]

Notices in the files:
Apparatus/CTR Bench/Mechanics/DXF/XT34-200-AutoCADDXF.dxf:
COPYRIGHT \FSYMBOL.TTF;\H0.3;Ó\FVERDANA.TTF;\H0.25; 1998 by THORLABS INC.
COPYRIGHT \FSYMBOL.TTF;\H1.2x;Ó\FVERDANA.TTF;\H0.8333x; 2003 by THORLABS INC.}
